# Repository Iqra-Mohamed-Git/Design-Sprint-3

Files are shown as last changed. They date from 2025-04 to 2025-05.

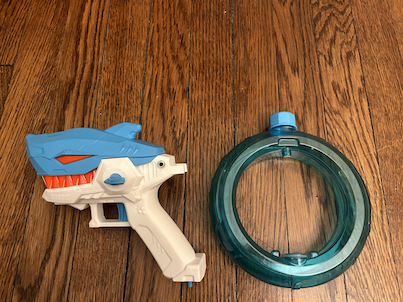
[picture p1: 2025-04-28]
Photos/Switch Adapted Water Gun Parts.png

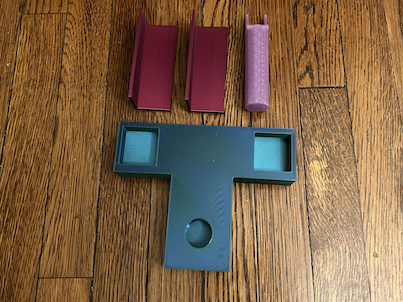
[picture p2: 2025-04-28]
Photos/Collapsible Stand Parts.png

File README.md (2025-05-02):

 <!--- TITLE --->
# Collapsible Water Gun Stand
<!--- Should match the name of the GitHub repository. Choose something descriptive rather than whimsical.  --->

## Overview
<!--- A brief summary of the project. What it does, who it is for, how much it costs. --->
The Collapsible Water Gun Stand is an assistive technology device that uses a switch to trigger the water gun to shoot water. The water gun sits on top of a stand that was 3D printed.

The device is comprised of an off-the-shelf water gun that was adapted to fit our needs and 3D printed parts. 

The Collapsible Water Gun Stand is open assistive technology (OpenAT). Under the terms of the open source licenses, the device may be built, used, and improved upon by anyone.

The overall cost of materials is about $23 (plus $6.99 for component shipping) 

Picture of Switch Adpated Water Gun with Collapsible Stand.

## Makers Making Change Assistive Device Library
<MMCWebLink>

## How to Obtain the Device
### 1. Do-it-Yourself (DIY) or Do-it-Together (DIT)

This is an open-source assistive technology, so anyone is free to build it. All of the files and instructions required to build the device are contained within this repository. Refer to the Maker Guide below.

## Build Instructions
<!--- Outline the major steps required to create a build --->

### 1. Read through the Maker Guide

The [Maker Guide](/Documentation/Switch_Adapted_Water_Gun_with_Collapsible_Stand_Maker_Guide.pdf)  contains all the necessary information to build this device, including tool lists, assembly instructions, and testing.

### 2. Order the Off-The-Shelf Components

The [Bill of Materials](/Documentation/Switch_Adapted_Water_Gun_with_Collapsible_Stand_BOM.csv) lists all of the parts and components required to build the device. 

### 3. Print the 3D Printable components

All of the files and individual print files can be found in the [/Build_Files/3D_Printing_Files](/Build_Files/3D_Printing_Files/) folder.

### 4. Assemble the Collapsible Water Gun Stand

Reference the Assembly Guide section of the [Maker Guide](/Documentation/Switch_Adapted_Water_Gun_with_Collapsible_Stand_Maker_Guide.pdf)  for the tools and steps required to build the device.

## How to improve this Device
As open source assistive technology, you are welcomed and encouraged to improve upon the design. 

## Files
### Documentation
<!--- Update the name, link, and version for documentation --->
| Document             | Version | Link |
|----------------------|---------|------|
| Design Rationale     | 1.0     | [Design Rationale](/Documentation/Switch_Adapted_Water_Gun_with_Collapsible_Stand_Design_Rationale.pdf)     |
| Maker Guide          | 1.0     | [Maker Guide](/Documentation/Switch_Adapted_Water_Gun_with_Collapsible_Stand_Maker_Guide.pdf)     |
| Bill of Materials    | 1.0     | [Bill Of Material](/Documentation/Switch_Adapted_Water_Gun_with_Collapsible_Stand_BOM.csv)     | 
| User Guide           | 1.0     | [User_Guide](/Documentation/Switch_Adapted_Water_Gun_with_Collapsible_Stand_User_Guide.pdf)    | 

<!---### Design Files
<!--- Include a copy of the original design files to facilitate easy editing and customization. Consider also including a generic format (e.g., STEP) --->

<!---### Build Files
<!--- Include a copy of the build files intended for manufacturing. This may include svg files for laser cutting, stl files for 3d printing, Gerber files for custom PCBs, and Arduino files for custom firmware. --->
<!--- - [3D Printing Files](/Build_Files/3D_Printing_Files)
 - [PCB Build Files](/Build_Files/PCB_Build_Files)
 - [Firmware Files](/Build/Firmware_Files)

## License
<!--- Add the year(s) for the copyright and the Designer Name. You may use the standard set of open licenses or choose your own for the hardware, software, and accompanying materials. --->
Copyright (c) 2025 Green Bean Team.

This repository describes Open Hardware:
 - Everything needed or used to design, make, test, or prepare the <DeviceName> is licensed under the [CERN 2.0 Weakly Reciprocal license (CERN-OHL-W v2) or later](https://cern.ch/cern-ohl ) .
 - All software is under the [GNU General Public License v3.0 (GPL-3.0)](https://www.gnu.org/licenses/gpl.html).
 - Accompanying material such as instruction manuals, videos, and other copyrightable works that are useful but not necessary to design, make, test, or prepare the <Device-Name> are published under a [Creative Commons Attribution-ShareAlike 4.0 license (CC BY-SA 4.0)](https://creativecommons.org/licenses/by-sa/4.0/) .

You may redistribute and modify this documentation and make products using it under the terms of the [CERN-OHL-W v2](https://cern.ch/cern-ohl).
This documentation is distributed WITHOUT ANY EXPRESS OR IMPLIED WARRANTY, INCLUDING OF MERCHANTABILITY, SATISFACTORY QUALITY AND FITNESS FOR A PARTICULAR PURPOSE.
Please see the CERN-OHL-W v2 for applicable conditions.

Source Location: [https://github.com/Iqra-Mohamed-Git/Design-Sprint-3/](https://github.com/Iqra-Mohamed-Git/Design-Sprint-3.git)

## Attribution
<!--- Provide any necessary attribution for designs or components that are included in the device or as part of the project. --->
The Interact Switch design by Mike Turvey is used under CC-BY 4.0. Instructions adapted from Original Interact Switch Assembly Instructions by Mike Turvey, used under CC-BY 4.0. 1 2 3 4 5 6 7 V1.1 | AUGUST 2023 Interact Switch ASSEMBLY GUIDE © 2023 by Neil Squire / Makers Making Change. This work is licensed under the CC BY SA 4.0 License: http://creativecommons.org/licenses/by-sa/4.0 Files available at 

<!--- This is the attribution for the template. --->
The documentation template was created by Makers Making Change / Neil Squire Society and is used under a CC BY-SA 4.0 license. It is available at the following link: [https://github.com/makersmakingchange/OpenAT-Template](https://github.com/makersmakingchange/OpenAT-Template)

### Contributors
<!--- List the names of the people that contributed to the design. This could include the original source of the idea, designers, testers, documenters, etc. --->
Designers:
 - Kayla Olivas
 - Sam Kenney
 - Zander Leong
 - Iqra Mohammed

Testers:
 - Kayla Olivas
 - Sam Kenney
 - Zander Leong
 - Iqra Mohammed

---
<!--- This is standard boilerplate for Makers Making Change. No changes should be required. --->
<!-- ABOUT MMC START -->
## This project was inspired by Makers Making Change, learn more about them here:
[Makers Making Change Logo](https://www.makersmakingchange.com/)

Makers Making Change is a program of [Neil Squire](https://www.neilsquire.ca/), a Canadian non-profit that uses technology, knowledge, and passion to empower people with disabilities.

Makers Making Change leverages the capacity of community based Makers, Disability Professionals and Volunteers to develop and deliver affordable Open Source Assistive Technologies.

 - Website: [www.MakersMakingChange.com](https://www.makersmakingchange.com/)
 - GitHub: [makersmakingchange](https://github.com/makersmakingchange)
 - Bluesky: [@makersmakingchange.bsky.social](https://bsky.app/profile/makersmakingchange.bsky.social)
 - Instagram: [@makersmakingchange](https://www.instagram.com/makersmakingchange)
 - Facebook: [makersmakechange](https://www.facebook.com/makersmakechange)
 - LinkedIn: [Neil Squire Society](https://www.linkedin.com/company/neil-squire-society/)
 - Thingiverse: [makersmakingchange](https://www.thingiverse.com/makersmakingchange/about)
 - Printables: [MakersMakingChange](https://www.printables.com/@MakersMakingChange)

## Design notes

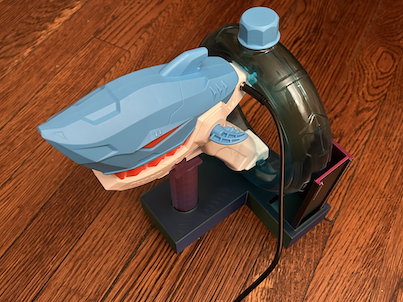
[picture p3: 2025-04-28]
Photos/Switch Adapted Water Gun with Collapsible Stand.png

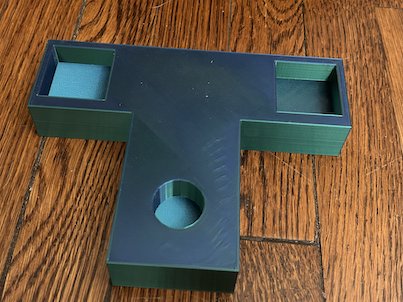
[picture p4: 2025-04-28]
Photos/Collapsible Stand Base.png

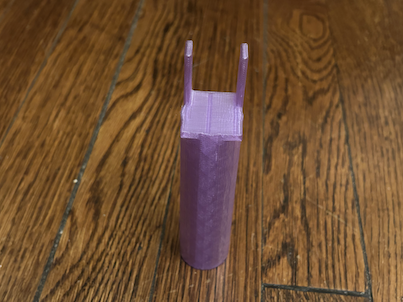
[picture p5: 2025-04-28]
Photos/Collapsible Stand Y Support.png

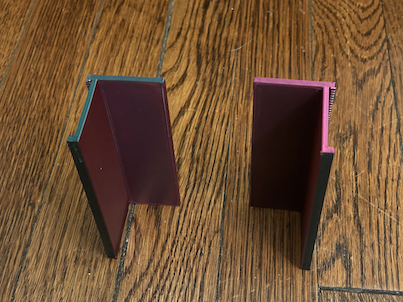
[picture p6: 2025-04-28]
Photos/Collapsible Stand L Supports.png

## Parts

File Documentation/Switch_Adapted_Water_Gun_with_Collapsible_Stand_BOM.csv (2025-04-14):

Device: | <Collapsible Water Gun Stand>
Version: | V<1.0.0>
Last Updated: | <April 2025>
 |  | Details | Cost | Link
ID | Electric Shark Water Gun | Walmart | $10 | https://www.walmart.com/ip/Tcovle-Electric-Shark-Water-Blaster-Super-Squirter-Fast-Fill-33-ft-Long-Range-Soaker-Toys-Summer-Swimming-Pool-Beach-Party-Backyard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
 | Shipping | Walmart | $6.99
 | 3.5 mm mono jack and nut | Approximate | $6
 | Copper Wire | Approximate | $2
 | 3D Printed Stand | 240 grams of filament, $20/kg | $4.80
 |  | Total cost Approximate | $30

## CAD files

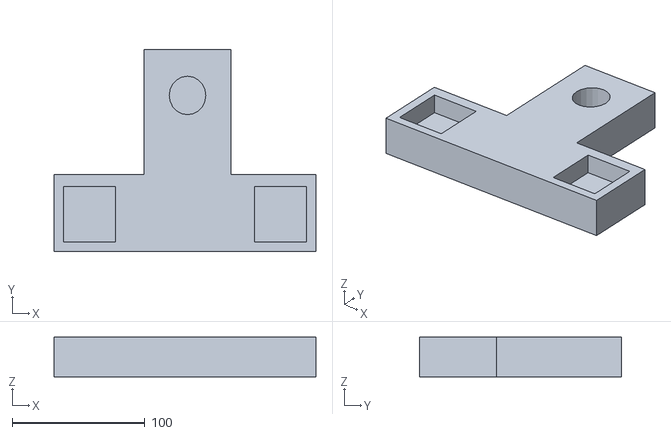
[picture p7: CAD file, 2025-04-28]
Build_Files/3D_Printing_Files/Collapsible Stand Base.stl
197.4 x 152.0 x 30.0

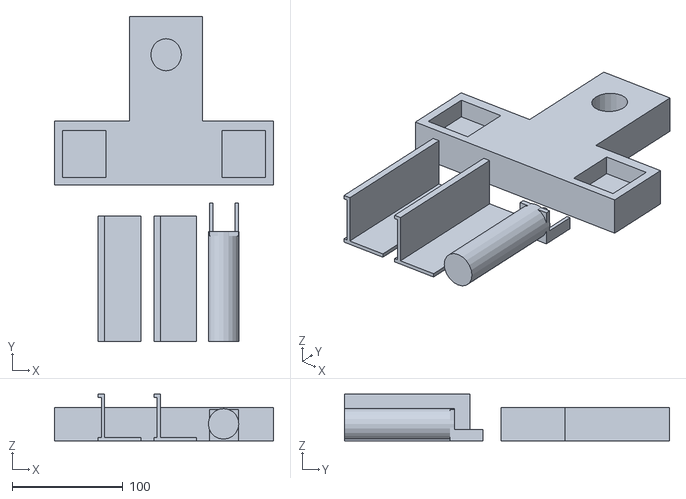
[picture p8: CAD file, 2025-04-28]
Build_Files/3D_Printing_Files/Collapsible Stand.stl
197.4 x 293.0 x 42.0

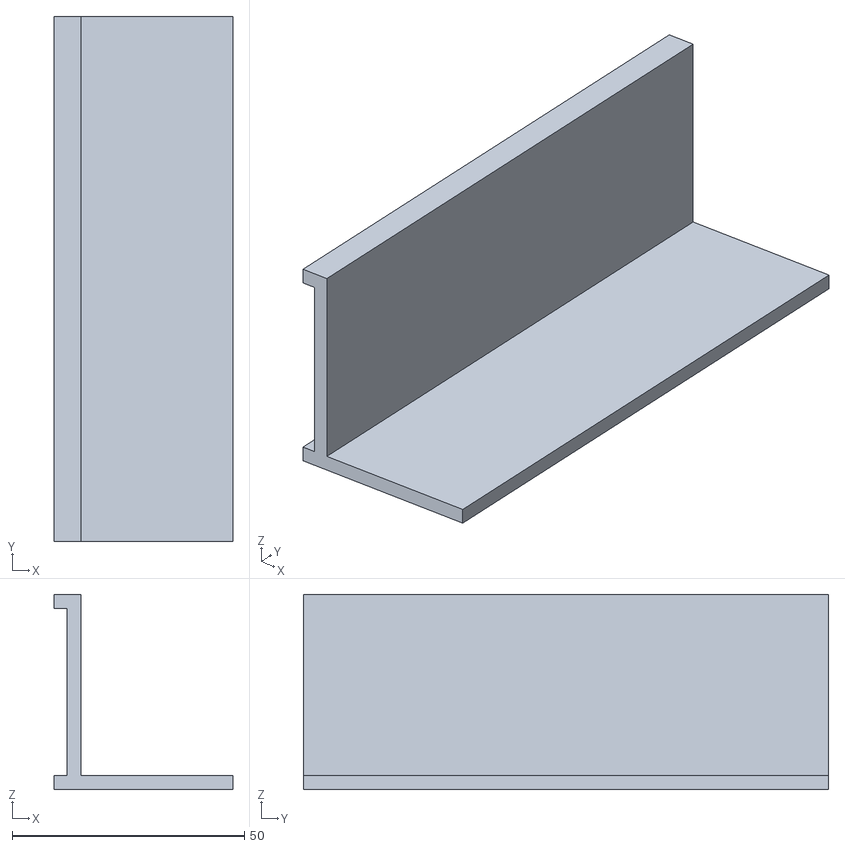
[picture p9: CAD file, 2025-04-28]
Build_Files/3D_Printing_Files/Collapsible Stand L Support Single.stl
38.5 x 113.0 x 42.0

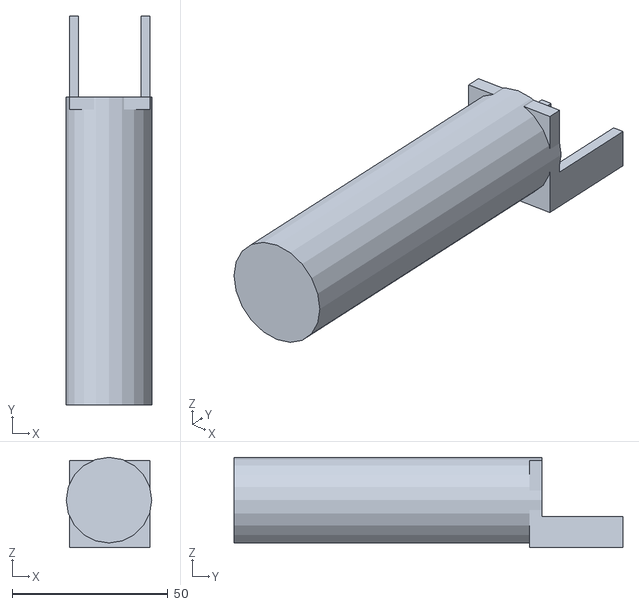
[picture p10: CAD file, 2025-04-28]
Build_Files/3D_Printing_Files/Collapsible Stand Y Support.stl
27.5 x 125.0 x 29.0

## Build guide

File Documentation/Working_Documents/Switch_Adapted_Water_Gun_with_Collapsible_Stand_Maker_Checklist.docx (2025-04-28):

# Maker Checklist created by Makers Making Change for Switch Adapted Water Gun (https://github.com/makersmakingchange/Switch-Adapted-Water-Gun/tree/main)

# Maker To Do List

- Read through the Assembly Guide to become familiar with required components, tools, supplies, and safety gear and overall assembly steps.
- Ask the User if they already own a 3.5mm switch – if they don’t, let them know that they can request one from the MMC library.
- Talk to the User about customization options (e.g., color, any special requests, etc.)
- Order hardware components.
- Gather tools, supplies, and safety equipment.
- Adapt the Water Gun.
- Print and assemble 3D Printed Water Gun Stand.
- Test device.
- Print “User Quick Guide.”

# Items to Give to User

- Adapted Water Gun.
- “User Quick Guide.”

© 2022 by Kerilyn Kennedy – Makers Making Change This work is licensed under the CC BY SA 4.0 License: http://creativecommons.org/licenses/by-sa/4.0 Files available at https://github.com/makersmakingchange/Switch-Adapted-Water-Gun/tree/main Page of

V1.0 | JUNE 2022 Switch Adapted Water Gun with Collapsible Stand MAKER CHECKLIST

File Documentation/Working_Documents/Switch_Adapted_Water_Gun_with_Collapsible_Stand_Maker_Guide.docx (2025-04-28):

Overview

This document contains the necessary information to build the Switch Adapted Water Gun with Collapsible Stand, a water gun that can be triggered via a switch and is supported by a stand that can be put together in pieces and be taken apart.

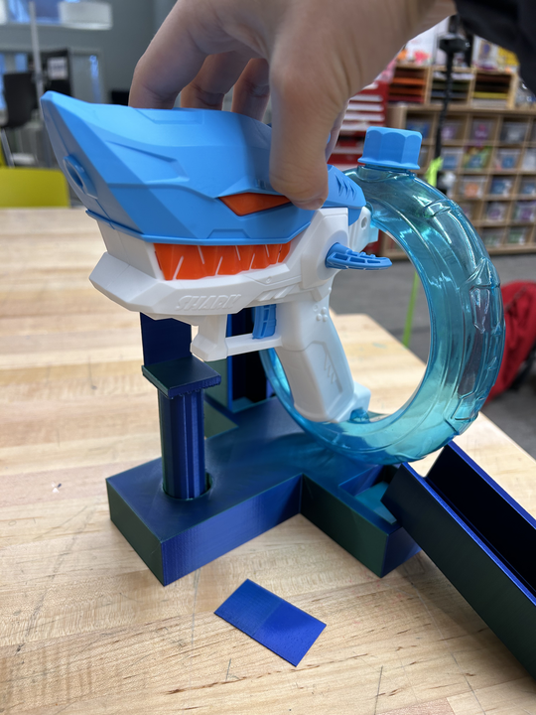
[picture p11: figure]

Printing Guide

This was originally printed on the Prusa MK4 using Prusa Slicer.

This device required supports on build plate only, 0.2mm STRUCTURAL, and 15% infill.

Printing Summary

Metrics
Total Print Time | 11 hours 42 minutes
Total Number of Components | 8 components
Typical Mass | 305.26 g
Typical Number of Print Setups | 5

The stand can also be separated into 3 files (4 prints) for reprinting.

File Name | Qty | Print Time | Mass (g) | Infill | Support | Layer Height | Notes
FullStand.stl | 1 | 9:44 | 239.22 | 15 | Y | 0.2 mm
Base.stl | 1 | 4:37 | 144.96 | 15 | N | 0.2 mm | part of FullStand
FrontSupport.stl | 1 | 1:46 | 28.85 | 15 | Y | 0.2 mm | part of FullStand
BackSupport.stl | 2 | 1:21 | 25.79 | 15 | N | 0.2 mm | part of FullStand
Interact_Switch_Base.stl | 1 | 0:50 | 17.85 | 15 | N | 0.2 mm
Interact_Switch_Insert.stl | 1 | 0:12 | 2.79 | 15 | N | 0.2 mm
ButtonCapInsert_0.3mm.stl | 1 | 0:03 | 0.74 | 15 | N | 0.2 mm | may need a different size
Interact_Switch_Cap_Plain.stl | 1 | 0:53 | 18.87 | 15 | Y | 0.2 mm | this print includes a customized switch

Post-Processing

Remove supports from the FrontSupport and ButtonCap. Inspect all pieces for print defects.

Examples of Quality Prints

| Base.stl
| FrontSupport.stl
| BackSupport.stl

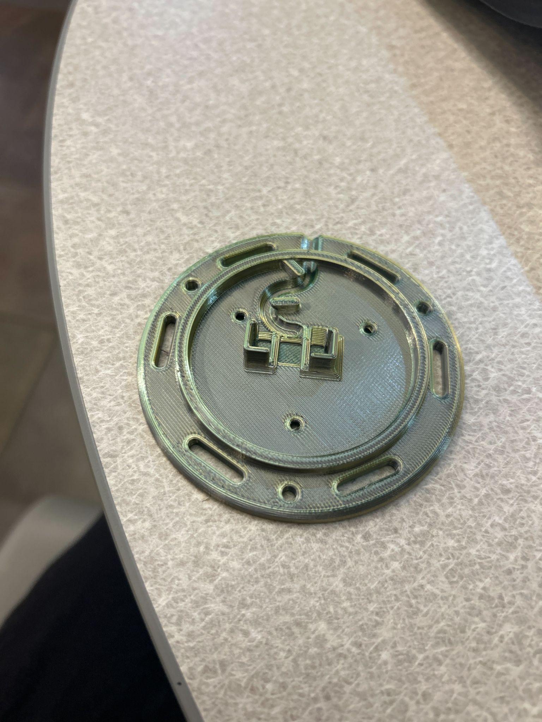
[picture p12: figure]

| Interact_Switch_Base.stl
| Interact_Switch_Insert.stl
| ButtonCapInsert_0.3mm.stl

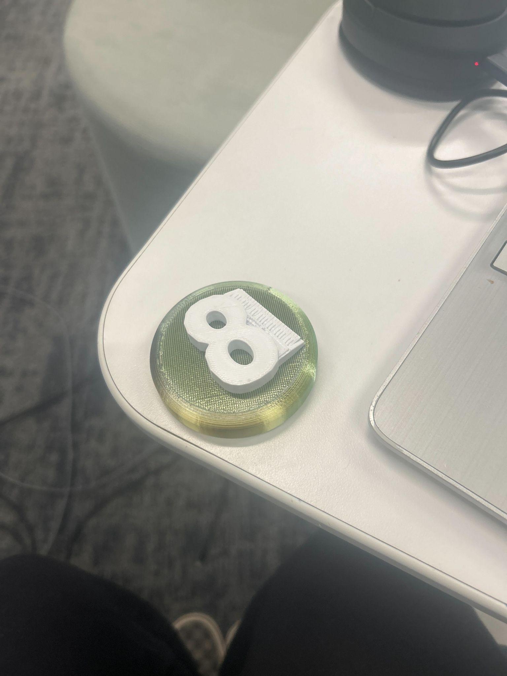
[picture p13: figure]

| Interact_Switch_Cap_Plain.stl

Assembly Guide

Part A: Disassembling the water gun

Required Components:

- Shark water gun

Required tools and Supplies:

- Screwdriver included in the box

Step A-01: Unscrew all the screws located on the gun’s surface by using the screwdriver included with the shark water gun.

Step A-02: Carefully remove all parts of the gun once the screws have been removed. Set these parts aside in a safe place, careful not to lose any of the screws.

Part B: Drilling a hole in the water gun

Required Components:

- Shark water gun

Required tools and Supplies:

- Screwdriver included in the box
- Electric drill
- Appropriate sized drill bit
- Soldering iron
- Solder
- Wire strippers
- Wire cutters
- Copper wire
- Sharpie
- Thick, wooden board

Required Personal Protective Equipment:

- Glasses

Step B-01: Take the white base of the water gun and mark a dot with a sharpie on the place that you will be drilling the hole for the socket. Make sure to leave enough surrounding space for the wires we will be putting on in a later step.

StepB-02: Once you are sure you have made enough space for the hole and it will be on a flat surface, hold the white base flat against a board.

StepB-03: Before handling the drill, place the glasses over your eyes to protect any debris from entering the eye socket.

StepB-03: Take the drill and apply pressure in the center of your mark and pull the trigger to create a hold in the base. Do this until you have fully pierced the white base of the water gun, then remove the drill by pressing on the trigger and pulling up.

Part C: Soldering the wires to the pre-existing wires in the water gun

Required Components:

- Shark water gun

Required tools and Supplies:

- Soldering iron
- Lead Solder
- Wire strippers
- Wire cutters
- Copper wire

Required Personal Protective Equipment:

- Glasses

Step C-01: Take about a four inch piece of twisted copper wire and strip off any protective coating that is around it.

Step C-02: Before beginning any soldering, place the protective glasses to protect any debris getting into the eyes.

Step C-03: To solder the copper wire to the existing wire, heat up the copper wire and apply the solder to the heated tip of the wire.

Step C-04: Quickly make contact to the pre-existing wire on the gun to solder the two pieces together.

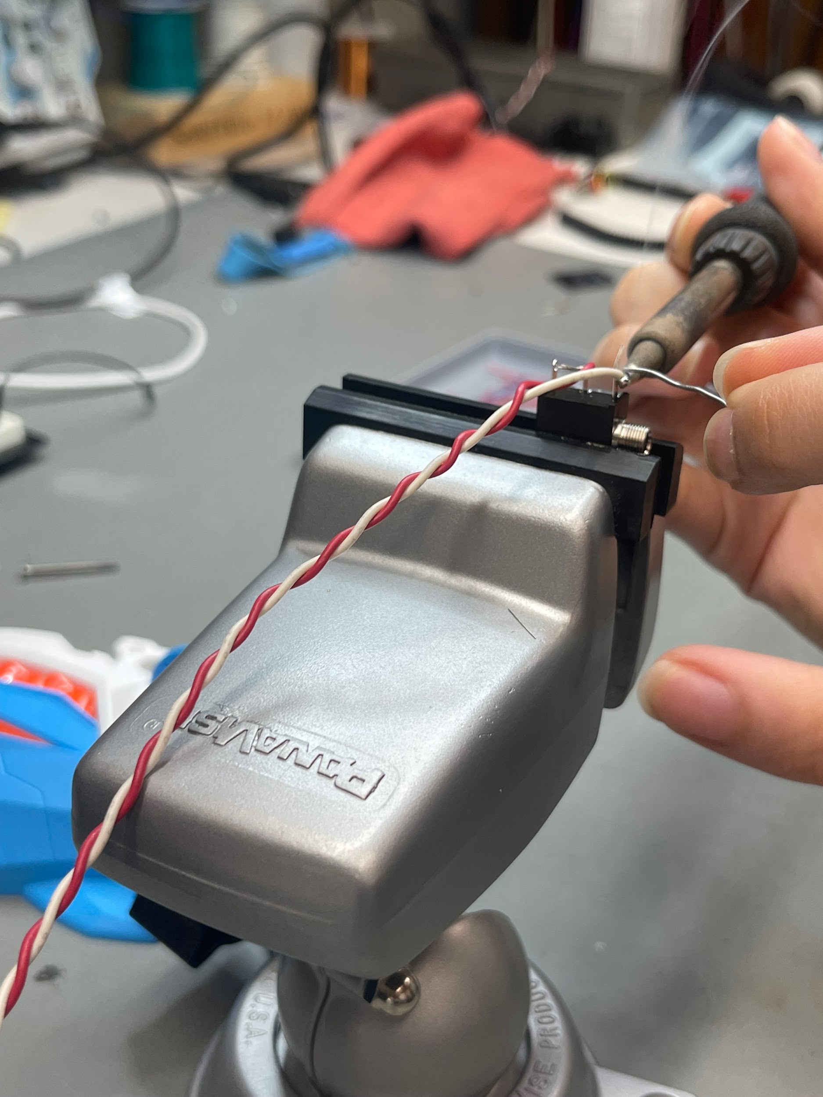
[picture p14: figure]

Step C-05: Following the same steps above on the opposite end of the copper wire, you will be soldering the copper wire to the jack.

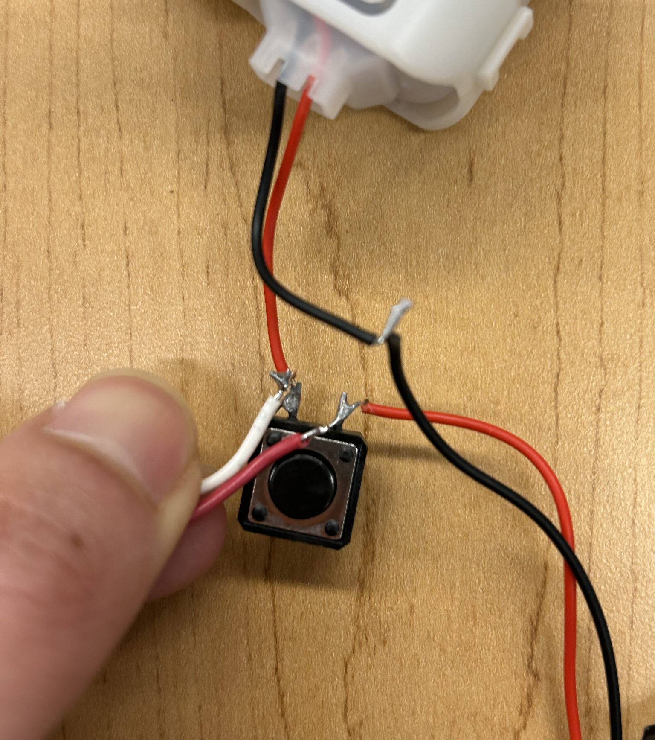
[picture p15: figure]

Step C-06: Fit the jack into the hole that was drilled into the white part of the gun earlier.

Step C-07: The gun can now be put together using the screwdriver and screws we used to take the gun apart in Step-A.

Part D: Adapting the switch

Required Components:

Required tools and Supplies:

- Screwdriver included in the box
- Electric drill
- Appropriate sized drill bit
- Soldering iron
- Solder
- Wire strippers
- Wire cutters
- Copper wire
- Sharpie
- Thick, wooden board

Required Personal Protective Equipment:

- Glasses

Step C-01: Take about a four inch piece of twisted copper wire and strip off any protective coating that is around it.

Step C-02: Before beginning any soldering, place the protective glasses to protect any debris getting into the eyes.

Step C-03: To solder the copper wire to the existing wire, heat up the copper wire and apply the solder to the heated tip of the wire.

Step C-04: Quickly make contact to the pre-existing wire on the gun to solder the two pieces together.

Step C-05: Following the same steps above on the opposite end of the copper wire, you will be soldering the copper wire to the jack.

Step C-06: Fit the jack into the hole that was drilled into the white part of the gun earlier.

Step C-07: The gun can now be put together using the screwdriver and screws we used to take the gun apart in Step-A.

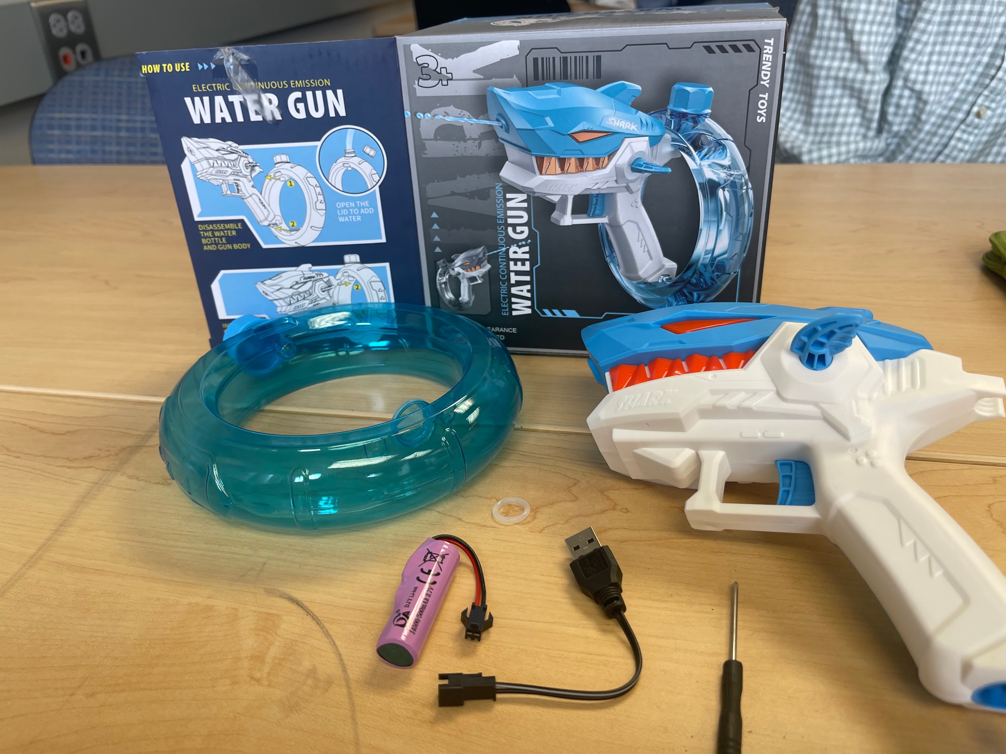
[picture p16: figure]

Part F: Assembling the switch

Required Components

1. 1x Switch Base (3D printed)

2. 1x Button Cap Holder (3D printed)

3. 1x Button Cap Insert (3D printed)

4. 1x Button Cap (3D printed)

5. 1x Omron SS-3GP limit switch

6. 1x 3.5 mm mono cable

7. 3x M2.5x12 or #4x 3-8” Pan Head screws (self threading)

Required Tools

• Soldering iron and solder

• Wire strippers

• Screw driver

• Safety glasses

Attribution

The Interact Switch design by Mike Turvey is used under CC-BY 4.0. Instructions adapted from Original Interact Switch Assembly Instructions by Mike Turvey, used under CC-BY 4.0. 1 2 3 4 5 6 7 V1.1 | AUGUST 2023 Interact Switch ASSEMBLY GUIDE © 2023 by Neil Squire / Makers Making Change. This work is licensed under the CC BY SA 4.0 License: http://creativecommons.org/licenses/by-sa/4.0 Files available at https://github.com/mwturvey/InteractSwitch

Assembly Instructions

Step 1 - Prep Cable

Cut off and discard one of the plugs from the mono audio cable. Use the wire strippers to carefully remove about 15 mm of the outer insulation from the end.

Step 2 - Prep Cable Wires Twist the copper strands together into a single wire. Use the wire strippers to remove roughly 5 mm of insulation from the other wire. (Note: Your cable may differ. If there are two wires with insulation, strip 5 mm from the end of each wire.)

Step 3 – Thread Cable into Switch Base

Thread the cable through the hole in the Switch Base. You will not be able to do this after you solder the limit switch onto the wire.

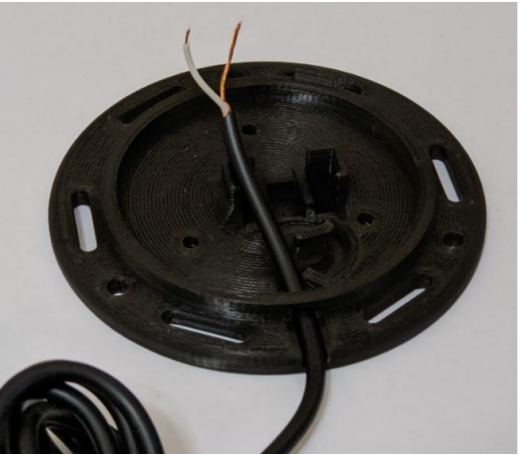
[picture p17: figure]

Step 4 – Solder Wires to Switch

Solder the wires into the switch in the position shown below. Note: Solder the two leads closest to the button on the switch. Test: plug your switch into a switch activated device and push the button on the limit switch

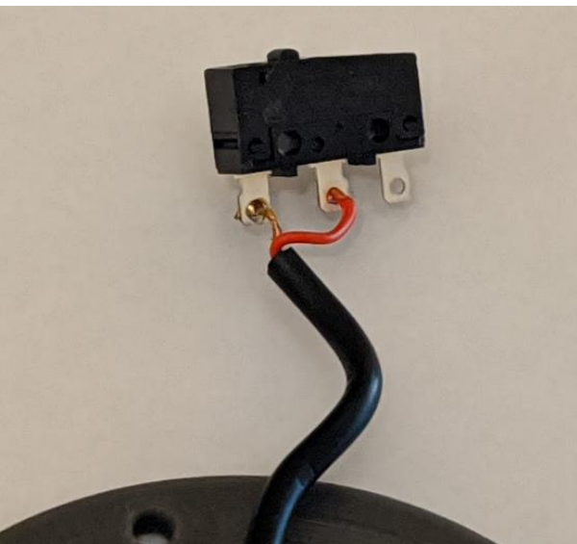
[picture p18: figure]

Step 5 – Position Switch in Base

Place the limit switch into the Switch Base as shown. For the orientation of the switch, when the cable is coming towards you, the button on the limit switch should be offset to the left. Make sure that no wires are stuck underneath, preventing the limit switch from going all the way down. Also push the cable in the slot as shown in the picture.

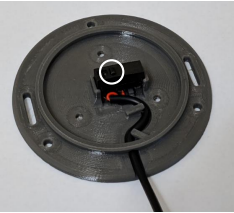
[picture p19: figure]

Step 6 – Assemble Button Cap

Turn the Button Cap over and insert the Button Cap Insert.

Step 7 – Finalize Button Cap Assembly

Insert the Button Cap Holder into the Button Cap Assembly. The orientation of the “open” side doesn’t matter. Note: for smoother switch action, sand the edges of the Button Cap Holder where it rubs on the switch. Check that the Insert is the right size. When placed on top of the base, it should be able to click the switch easily and not be overly wobbly.

Step 8 – Assemble Switch

Align the three posts of the Switch Cap Holder to the three holes in the Switch Base. Secure the Switch Cap Holder to the Switch Base using three screws. Note: Be careful not to over tighten the screws. Tighten them until you notice the resistance increases and the Switch Cap Holder is firmly against the Switch Base.

Testing

The last thing to do is test your switch. If this is your first switch, you’ll likely need to test it out and figure out the best size of Switch Cap Insert to use. The first thing I do to test a switch is to push it a lot. Tap it everywhere, repeatedly. Every time you push it, you should hear it click down and click as it goes back up. It should never stick. If you wiggle the top, it should move some, but it shouldn’t feel like it’s rattling around. Next, plug the switch into a switch activated device and make sure that it works.

Troubleshooting

Problem | Solution
The switch cap is too loose and rattles around easily. | Use a larger/ thicker Switch Cap Insert.
Switch doesn’t make any noise when pushed. | Use a smaller/ thinner Switch Cap Insert. An insert that is too big can cause the limit switch to be always depressed. When this is the case, you’ll often hear the limit switch “click” closed when you’re screwing everything together, but it won’t ever click open.
Switch sticks/ doesn’t always go back up. | Use a smaller/ thinner Switch Cap Insert. You may likely need just one size thinner.
Switch makes clicking noise, but the switch activated device isn’t activating | • Test the switch activated device with a switch known to work, just to make sure it’s working fine. • Check that the plug is firmly plugged into the device • The solder connection may be bad and need to be re-soldered. • There may be an internal break in the wire, and you will need to replace it. This is a particularly common failure point for an older switch.

Part D: Assembling the water gun

Required Components:

- Adapted Shark water gun
- 3D Printed Base (4 pieces)
- Switch

Step D-01: Take the parts of the 3D printed base and stick them into the sockets that fit their shape, making sure to have the hollowed out part of the rectangular stands facing inwards.

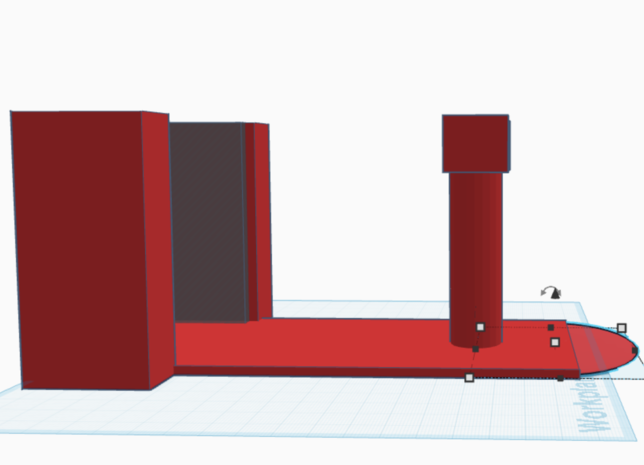
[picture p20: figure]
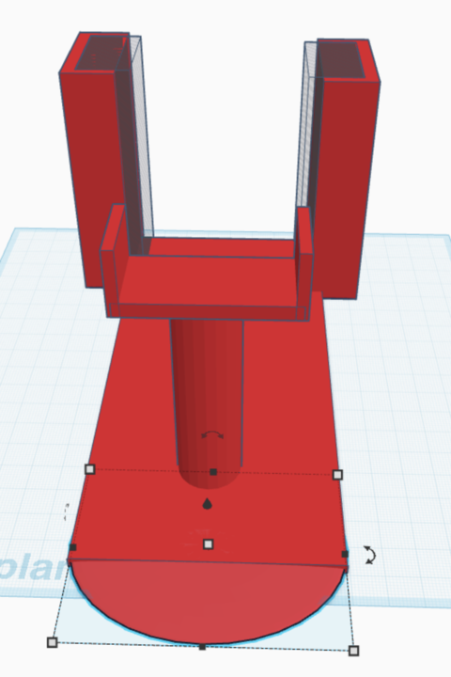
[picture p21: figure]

Step D-02: Place the gun on the stand, making sure to have the water tank fit inside the rectangular stands and the front end of the gun rest on top of the cylindrical stand.

Step D-03: Plug the switch into the jack that we made onto the gun and set the button flat on your workstation.

Step D-04: You are now able to activate your gun by clicking on the switch or pulling the trigger.

Testing

The last thing to do is test the water gun. Ensure that the port of the switch is fully inserted into the jack that you adapted on the jack. Before you fit the water gun onto the stand, fill the tank up with tap water. Once the gun is filled, place it onto the stand, making sure it fits snug. Either by holding the base in one hand or leaving it on top of a flat surface, take the button in the other hand and press down on it. This should trigger the gun to release water. Additionally, you can pull back the trigger to release water.

V 1.0.0 | APRIL 2025 Switch Adapted Water Gun with Collapsible Stand MAKER GUIDE

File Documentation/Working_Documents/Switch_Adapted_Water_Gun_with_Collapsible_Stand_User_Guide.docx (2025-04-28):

# Switch Adapted Water Gun with Collapsible Stand

## USER GUIDE

### Introduction

This is a switch adapted water gun that is compatible with 3.5mm switches. This device may be beneficial to someone with limited hand function that is interested in using a water gun.

### Features

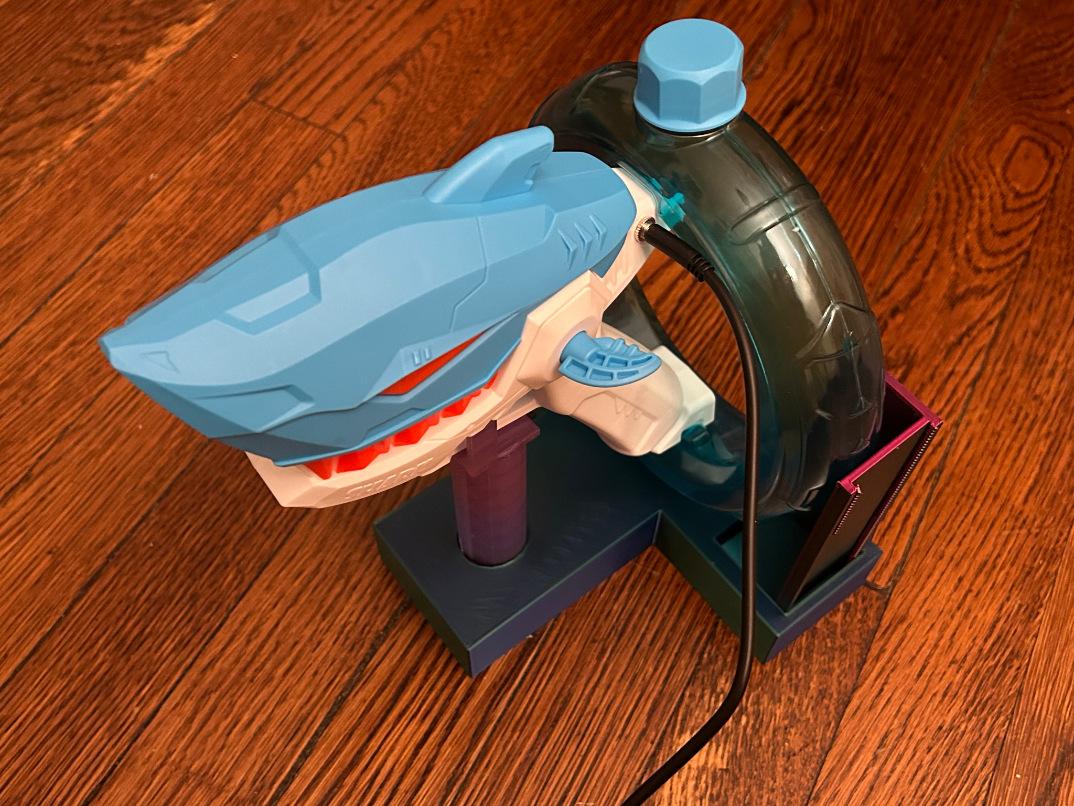
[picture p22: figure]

Water compartment

Battery component

Nozzle

3.5 mm. mono jack

3D printed stand

Usage

The Switch Adapted Water Gun with Collapsible Stand can be used by first filling it up with water. Next, plug in a 3.5mm switch into the back of the water gun. Once the switch is pressed, the water gun is activated.

### Compatibility

The Switch Adapted Water Gun with Collapsible Stand should be compatible with any 3.5mm switch.

### Specifications

Length (mm) | Width (mm) | Height (mm) | Mass (g)
193 | 87 | 130 | 480

*The mass given is the mass of the empty water gun.

### Cleaning

The device can be wiped down with a damp cloth. When not in use, empty out the water compartment in the gun.

# Switch Adapted Water Gun

## USER QUICK GUIDE

### Changing the Batteries

The batteries can be accessed by unscrewing all the screws located on the gun"s surface. Once they have been removed, open up the gun and access the white cylinder which contains the rechargeable batteries and the charging cable. The batteries can be charged with a usb. The battery shouldn't be charging for a prolonged time.

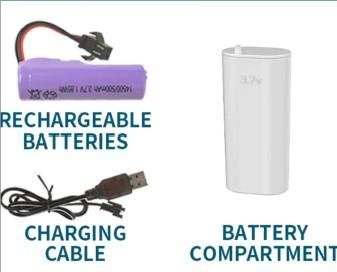
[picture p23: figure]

Page PAGE 1 of 2

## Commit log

2025-04-09 add template files
    [Device_Name_BOM.csv, Device_Name_BOM.xlsx, OpenAT_Placard.f3d, OpenAT_Placard.stl]
2025-04-28 Update documentation, add photos, clean up files
    [Base.stl, Collapsible Stand Base.stl, Collapsible Stand L Support Single.stl, Collapsible Stand Y Support.stl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]
